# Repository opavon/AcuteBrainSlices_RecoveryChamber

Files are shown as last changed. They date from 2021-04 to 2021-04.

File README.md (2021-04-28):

# Recovery Chamber to incubate Acute Brain Slices

This is a parts list to ass assemble a recovery chamber to incubate acute brain slices prepared as described in Oriol Pavon Arocas, Tiago Branco (2021). Preparation of acute midbrain slices for patch-clamp recordings. [https://dx.doi.org/10.17504/protocols.io.bukhnut6].

To assemble a recovery chamber you will need the following:
* Glass beaker, 150 mL, 60 mm external diameter (Borosilicate glass with spout, Cat. No. 213-1123, VWR).
* Microfilter candles (or bubblestones) to bubble solutions: 6 mm diameter, porosity P3, narrow glass tube (Cat. No. ROBU18103, Robuglas).
* Plastipak luer slip syringe (2 mL, sterile, Cat. No BD574 or BDS0003, Appleton Woods). We cut the tip so it has the right length and insert a stainless steel needle (e.g. brown - BD Microlance 3, 26G, 0.45x13 mm, Cat. No. 303800) at the bottom to make a support for the bubblestone.
* Sterile gauze swabs (10x10 cm, 8 ply, Cat. No. MSPPEJE136 or IBSA25071, VWR).
* Double threaded plastic cap (Samco™ Narrow Mouth Bio-Tite™ 90mL (3 oz.) 48mm Specimen Containers, Sterile, Cat. No. 020039, Thermo Fisher).

Alternatively, if plastic caps of the correct size can't be found, you can use the 3D printed pieces available at this repository.
* __Recovery_Chamber.step__ - design of the pieces. They fit the 150 mL beaker listed above.
* __Recovery_Chamber_outer_piece.stl__ - we print it on a Ultimaker S5.
* __Recovery_Chamber_inner_piece.stl__ - we print it on a Ultimaker S5.

The 3D printed pieces we currently use for the recovery chamber were designed by Robb Barrett from the Fabrications Lab at the Sainsbury Wellcome Centre (UCL) and can be downloaded from this repository. The *.stl* and *.step* files are made available under a CC0-1.0 license. We hope this will be a far cheaper and easy to assemble alternative to the commercially available recovery chambers.

-----

Below are some images of how the 3D printed pieces and the assembled recovery chamber look like:




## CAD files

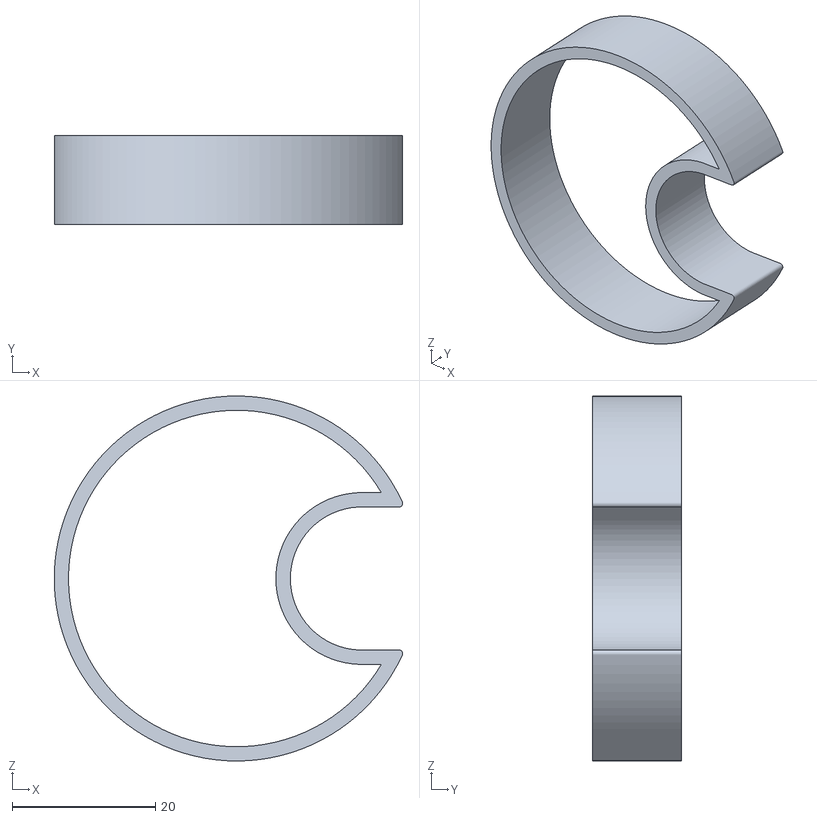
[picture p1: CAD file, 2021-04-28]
Recovery_Chamber_inner_piece.stl
48.7 x 12.5 x 51.0

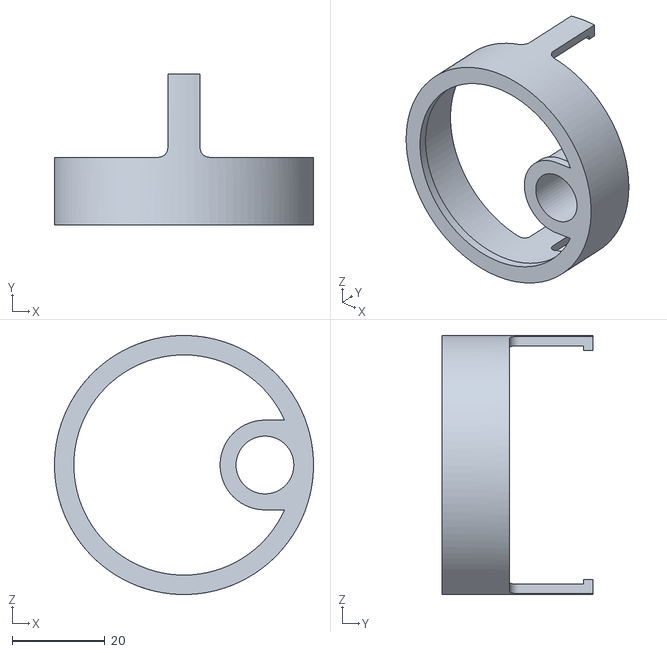
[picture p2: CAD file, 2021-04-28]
Recovery_Chamber_outer_piece.stl
56.0 x 32.6 x 56.0

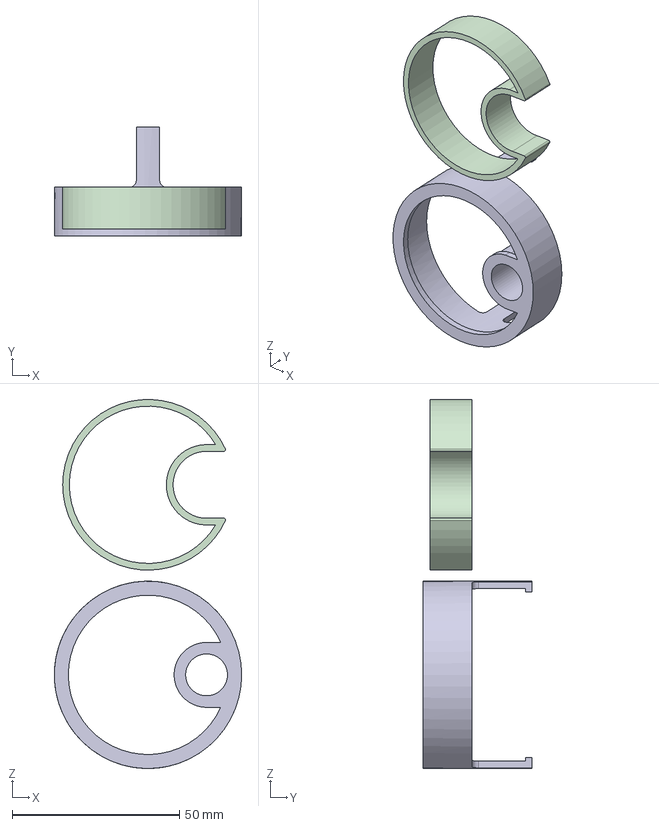
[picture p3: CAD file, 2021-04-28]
Recovery_Chamber.step
56.0 x 32.6 x 110.3 mm
